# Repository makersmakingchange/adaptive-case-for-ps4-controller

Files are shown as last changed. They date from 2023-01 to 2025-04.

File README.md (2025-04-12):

# Adaptive Case for PS4 Controller
The Adaptive Case for PS4 Controller is an inexpensive and non-destructive controller modification designed to make the stock PS4 controller more accessible. This device aims to assist those with limited hand dexterity by enlarging and spreading out the buttons on the PS4 controller. This device can be mounted to a surface so that both hands can freely operate the controls.   

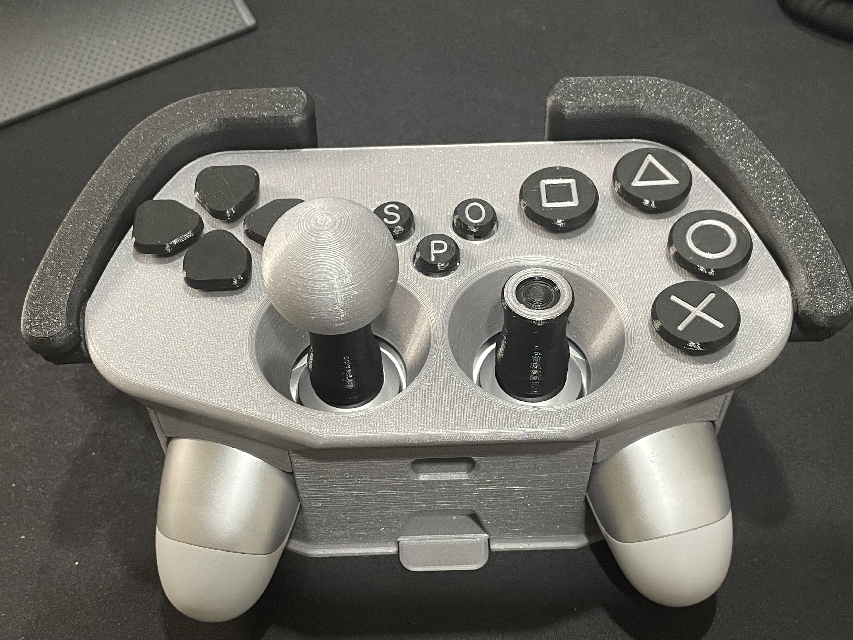
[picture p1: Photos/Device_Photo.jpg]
Picture of a black and gray Adaptive Case for PS4 Controller


## More info at
- [Makers Making Change Project Page](https://makersmakingchange.com/project/adaptive-case-for-ps4-controller)

## How to Obtain an Adaptive Case for PS4 Controller
### 1. Do it Yourself (DIY) or Do it Together (DIT)

This is an open-source assistive technology, so anyone is free to build it. All of the files and instructions required to build the Adaptive Case for PS4 Controller are contained within this repository. Refer to the Maker Checklist below.

### 2. Request a build of this device

If you would like to obtain an Adaptive Case for PS4 Controller , you may submit a build request through the [MMC Library Page](https://makersmakingchange.com/project/adaptive-case-for-ps4-controller/). The requestor is responsible for the cost of materials and any shipping.

### 3. How to build this device for someone else

If you have the skills and equipment to build this device, and would like to donate your time to create the switch for someone who needs it, visit the [MMC Maker Wanted](https://makersmakingchange.com/maker-wanted/) section.

## Getting Started

### 1. Read the Makers Checklist

The Makers Checklist contains a list of tasks to complete to build the device.

### 2. Print the 3D Printable components

All of the files and individual print files can be in the [/Build_Files/3D_Printing_Files](/Build_Files/3D_Printing_Files/) folder.

### 3. Assemble the Adaptive Case for PS4 Controller

Reference the [Assembly Guide](/Documentation/Adaptive_Case_for_Ps4_Controller_Assembly_Guide.pdf) for the tools and steps required to build each portion.

## Files
### Documentation
| Document             | Version | Link |
|----------------------|---------|------|
| Design Rationale     | 1.0     | [Adaptive_Case_for_Ps4_Controller_Design_Rationale](/Documentation/Adaptive_Case_for_Ps4_Controller_Design_Rationale.pdf)     |
| Maker Checklist      | 1.0     | [Adaptive_Case_for_Ps4_Controller_Maker_Checklist](/Documentation/Adaptive_Case_for_Ps4_Controller_Maker_Checklist.pdf)     |
| Bill of Materials    | 1.0     | [Adaptive_Case_for_Ps4_Controller_Bill_of_Materials](/Documentation/Adaptive_Case_for_Ps4_Controller_BOM.xlsx)     |
| 3D Printing Guide    | 1.0     | [Adaptive_Case_for_Ps4_Controller_3D_Printing_Guide](/Documentation/Adaptive_Case_for_Ps4_Controller_3D_Printing_Guide.pdf)   |
| Assembly Guide       | 1.0     | [Adaptive_Case_for_Ps4_Controller_Assembly_Guide](/Documentation/Adaptive_Case_for_Ps4_Controller_Assembly_Guide.pdf)     |
| User Guide           | 1.0     | [Adaptive_Case_for_Ps4_Controller_User_Guide](/Documentation/Adaptive_Case_for_Ps4_Controller_User_Guide.pdf)    |
| Changelog            | 1.0     | [Adaptive_Case_for_Ps4_Controller_Changelog](/Documentation/Adaptive_Case_for_Ps4_Controller_Changelog.pdf)     |

### Design Files
- [CAD Files](/Design_Files)

### Build Files
 - [3D Printing Files](/Build_Files/3D_Printing_Files)

## Attribution

Design: [Cisco](https://www.printables.com/social/28161-cisco/models) posted on [Printables](https://www.printables.com/model/91884-ps4-case-adapter)

Documentation by Neil Squire / Makers Making Change.

## License
Everything needed or used to design, make, test, or prepare theAdaptive_Case_for_Ps4_Controller is licensed under the CERN 2.0 Permissive license <https://ohwr.org/project/cernohl/wikis/Documents/CERN-OHL-version-2> (CERN-OHL-P) . 

Accompanying material such as instruction manuals, videos, and other copyrightable works that are useful but not necessary to design, make, test, or prepare the Adaptive_Case_for_Ps4_Controller are published under a Creative Commons Attribution-ShareAlike 4.0 license https://creativecommons.org/licenses/by-sa/4.0/ (CC BY-SA 4.0).

---

<!-- ABOUT MMC START -->
## About Makers Making Change
[Makers Making Change Logo](https://www.makersmakingchange.com/)

Makers Making Change is a program of [Neil Squire](https://www.neilsquire.ca/), a Canadian non-profit that uses technology, knowledge, and passion to empower people with disabilities.

Makers Making Change leverages the capacity of community based Makers, Disability Professionals and Volunteers to develop and deliver affordable Open Source Assistive Technologies.

 - Website: [www.MakersMakingChange.com](https://www.makersmakingchange.com/)
 - GitHub: [makersmakingchange](https://github.com/makersmakingchange)
 - Bluesky: [@makersmakingchange.bsky.social](https://bsky.app/profile/makersmakingchange.bsky.social)
 - Instagram: [@makersmakingchange](https://www.instagram.com/makersmakingchange)
 - Facebook: [makersmakechange](https://www.facebook.com/makersmakechange)
 - LinkedIn: [Neil Squire Society](https://www.linkedin.com/company/neil-squire-society/)
 - Thingiverse: [makersmakingchange](https://www.thingiverse.com/makersmakingchange/about)
 - Printables: [MakersMakingChange](https://www.printables.com/@MakersMakingChange)

### Contact Us
For technical questions, to get involved, or to share your experience we encourage you to [visit our website](https://www.makersmakingchange.com/) or [contact us](https://www.makersmakingchange.com/s/contact).
<!-- ABOUT MMC END -->

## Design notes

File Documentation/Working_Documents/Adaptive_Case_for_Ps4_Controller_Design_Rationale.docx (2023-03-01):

# Introduction

The Adaptive Case for PS4 Controller is an inexpensive and non-destructive controller modification designed to make the stock PS4 controller more accessible. This device aims to assist those with limited hand dexterity by enlarging and spreading out the buttons on the PS4 controller. This device can be mounted to a surface so that both hands can freely operate the controls.

# Research

Device | Price | Notes | Link

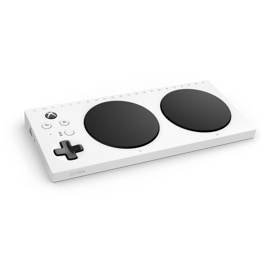
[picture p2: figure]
Angled view of Xbox Adaptive Controller

XAC – Commercial | ~$130 CA | The Xbox adaptive controller allows users with limited dexterity fully customize their gaming set up with different assistive switches and joysticks. This device costs around $130 plus the additional cost of external devices. | Xbox Adaptive Controller | Xbox (https://www.xbox.com/en-CA/accessories/controllers/xbox-adaptive-controller)

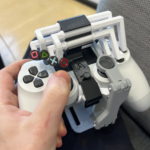
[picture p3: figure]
A hand holding a white PS4 controller with 3D printed one handed controls

One Handed Ps4 Controller | DIY | This DIY device is inexpensive and fully 3D printed. It targets users with one hand or users with more dexterity in one hand. | One-handed DualShock 4 by Akaki | Download free STL model | Printables.com (https://www.printables.com/model/126646-one-handed-dualshock-4) One-handed PS4 Controller Modification - Makers Making Change (https://makersmakingchange.com/project/one-handed-ps4-controller-modification/)

# Requirements

## Goals

G01 | Allow users with limited hand dexterity operate the PS4 controller
G02 | Nondestructively modify the PS4 controller to make it more accessible
G03 | Assist users who find it challenging to hold a controller

## Functional Requirements

F01 | Must fit the standard PS4 controller (DualShock 4)
F02 | Must allow users to operate the PS4 controller with limited dexterity and force

## Non-functional Requirement

NF01 | Must be easy to clean

## Constraints

C01 | Must be printable on standard Maker 3D printers

# Version 1.0

The Adaptive Case for PS4 Controller is designed by Cisco (https://www.printables.com/social/28161-cisco/models) on Printables (https://www.printables.com/model/91884-ps4-case-adapter) under the GNU GENERAL PUBLIC LICENSE (https://www.gnu.org/licenses/old-licenses/gpl-2.0.html).

This device encapsulates the controller in an adaptive case that can be mounted to a surface, so users do not need to hold the controller. It has multiple joystick options to help tailor the device to the user.

## Device Testing

### Assembling

- Little difficult to feed in Button Tails
  - Broke R1 tail while feeding into its slot.
  - Using sandpaper to smooth rough parts on these tails helps.
  - Using a zip tie to clear the tunnels also helps.
  - May take a few extra tails to install properly.
  - Once installed, they work great.
- Joysticks
  - Very secure when properly attached.
  - Very difficult to thread screws into joystick toppers.
  - Broke two different mounting screw while attaching the joysticks to the controller.
  - Threads broke off inside the joystick toppers. All had to be reprinted.

Notes: The designer has been contacted and is willing to modify the print files so threads can be printed sideways to increase strength. The designer will also increase the thread tolerances to make the joysticks easier to attach.

Update: Fusion360 files have been updated to add 0.15mm clearance to the joystick threads. This has been tested on multiple printers and is working well.

### Operating

- All buttons worked as intended.

# Opportunities for Improvement

- Allow Touch Pad to be pressed.
- As only L2 and R2 bumpers can be triggered, it would be nice to allow access to the L1 and R1 bumpers.

© 2023 by Neil Squire / Makers Making Change This work is licensed under the CC BY SA 4.0 License: http://creativecommons.org/licenses/by-sa/4.0 Files available at https://makersmakingchange.com/project/adaptive-case-for-ps4-controller Page 1 of 1

V1.0 | February 2023 Adaptive Case for PS4 Controller Design Rationale

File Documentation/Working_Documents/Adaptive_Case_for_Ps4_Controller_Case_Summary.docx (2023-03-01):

# Title

Adaptive Case for PS4 Controller

## Subtitle

An inexpensive and non-destructive controller modification designed to make the stock PS4 controller more accessible.

Device Specifications

Build Time:

< 1hr

1-4 hr

5-10hr

>10hr

Cost:

$0 - $10

$11 - $25

$26 - $50

$51 - $100

$101 - $250

$250+

Stage: Recently Added

Skills: 3D Printing

Need:

Disability: Mobility / Physical

Difficulty: Intermediate

License: GNU GENERAL PUBLIC LICENSE (https://www.gnu.org/licenses/old-licenses/gpl-2.0.html)

Usages: ADL, Recreation and Leisure, Computer Access

Type:

Designer:

## Device Details

### Overview

The Adaptive Case for PS4 Controller is an inexpensive and non-destructive controller modification designed to make the stock PS4 controller more accessible. This device aims to assist those with limited hand dexterity by enlarging and spreading out the buttons on the PS4 controller. This device can be mounted to a surface so that both hands can freely operate the controls.

### Compatibility

Note that the PS4 controller can be used for PC based gaming.

Platforms: PlayStation 4, PC

Controllers: DualShock 4 Controller

### Usage

The case can be opened to insert the PS4 controller and snapped shut to secure it. 3D printed mounting screws are placed around the joysticks on the controller before screwing on various attachments. The device also comes with a low-profile dock that can be used to secure the adaptive case to a surface.

### Cost

Approximately $8 for filament

### Build Instructions

The build involves assembling 3D printed components. No commercial hardware is needed.

#### Skills Required

- 3D Printing

#### Time Required

- Total 3D Printing Time: 38h 20min
- Assembly Time: 10m

#### Tools

- Eye Protection
- Hobby Knife
- Sandpaper
- Superglue
- Tape
- Zip Ties

#### 3D Printing

- 1X All_Button_Faces.stl
- 1X Button_Tails.stl
- 1X Case.stl
- 1X Dock.stl
- 1X Face.stl
- 1X Joystick.stl
- 1X Trigger.stl

### Attribution

Design by Cisco (https://www.printables.com/social/28161-cisco/models) posted on Printables (https://www.printables.com/model/91884-ps4-case-adapter) under the GNU GENERAL PUBLIC LICENSE (https://www.gnu.org/licenses/old-licenses/gpl-2.0.html)

Documentation: Neil Squire / Makers Making Change

© 2023 by Neil Squire / Makers Making Change This work is licensed under the CC BY SA 4.0 License: http://creativecommons.org/licenses/by-sa/4.0 Files available at https://makersmakingchange.com/project/adaptive-case-for-ps4-controller Page 1 of 4

V1.0 | February 2023 Adaptive Case for PS4 Controller Summary

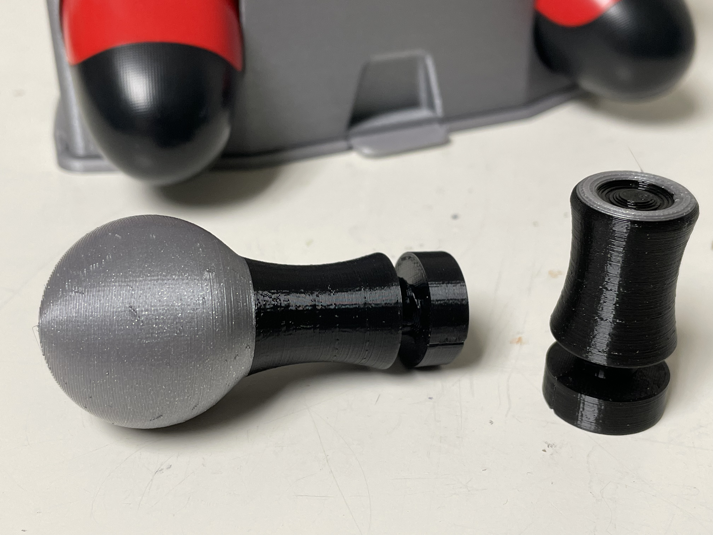
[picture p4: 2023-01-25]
Photos/Joysticks.jpeg

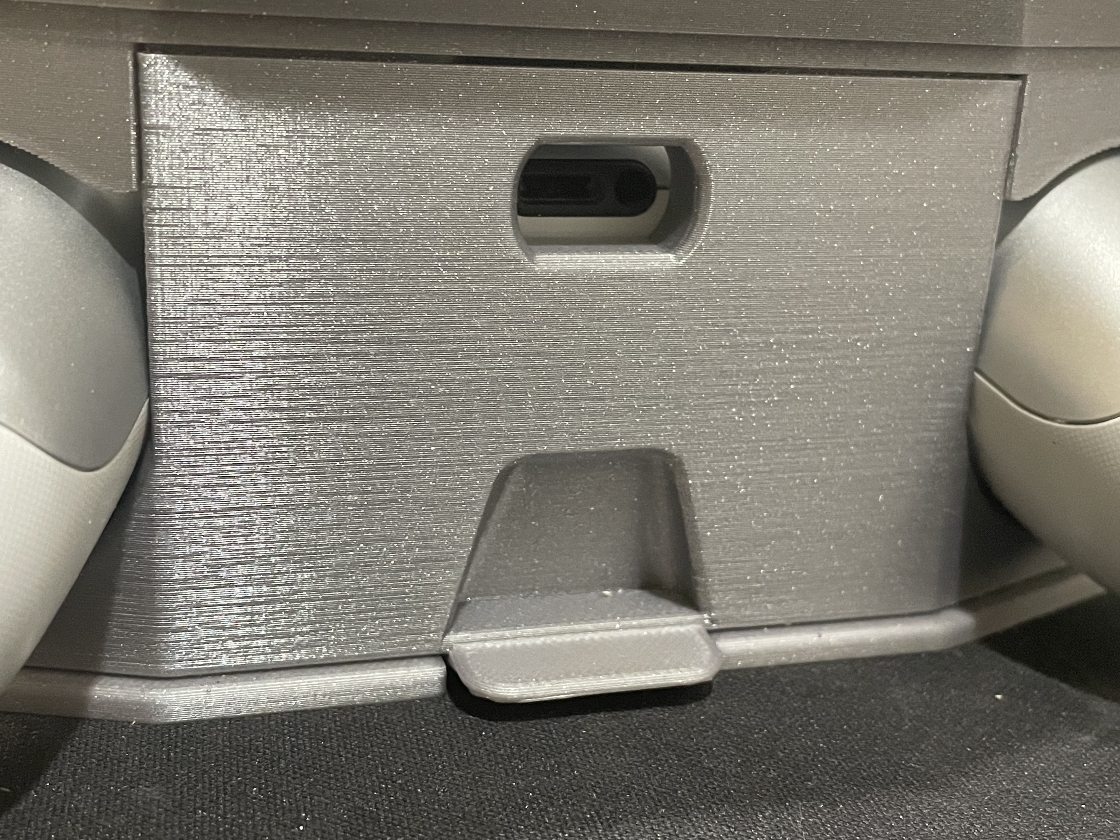
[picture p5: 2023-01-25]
Photos/Unlocking Dock.jpeg

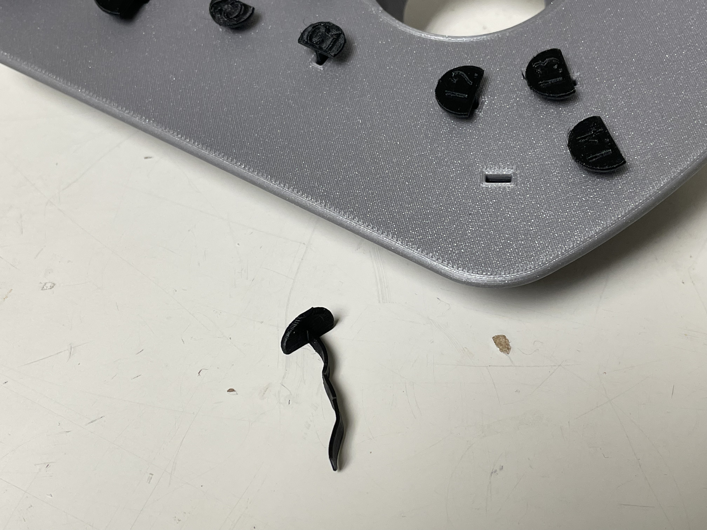
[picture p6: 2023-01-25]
Photos/Broken Tail.jpg

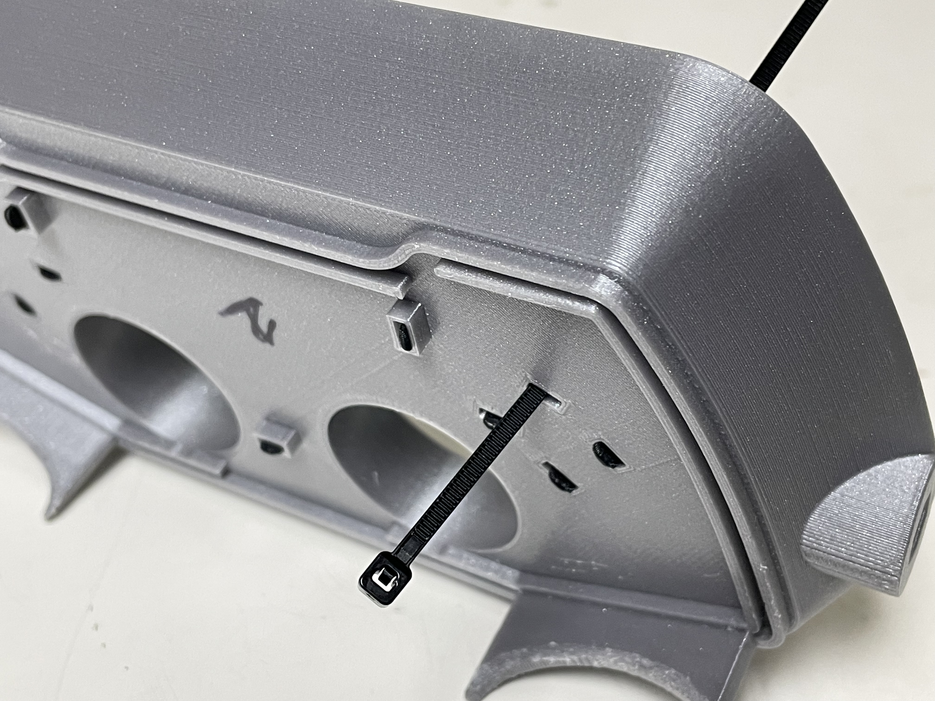
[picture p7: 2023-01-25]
Photos/Plugged Tunnel.jpg

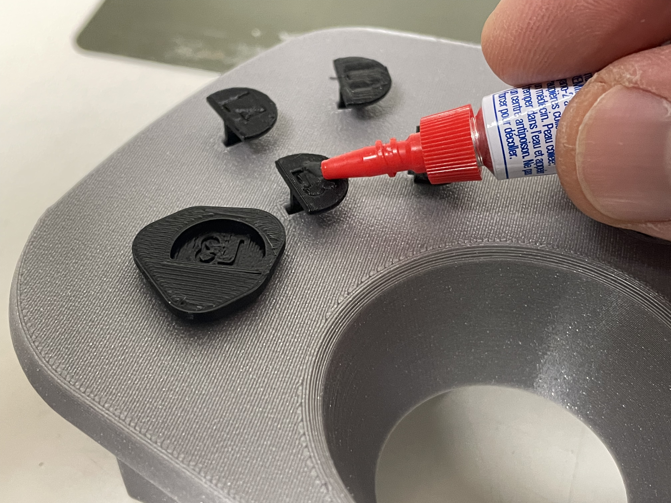
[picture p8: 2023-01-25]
Photos/Gluing Button Faces.jpg

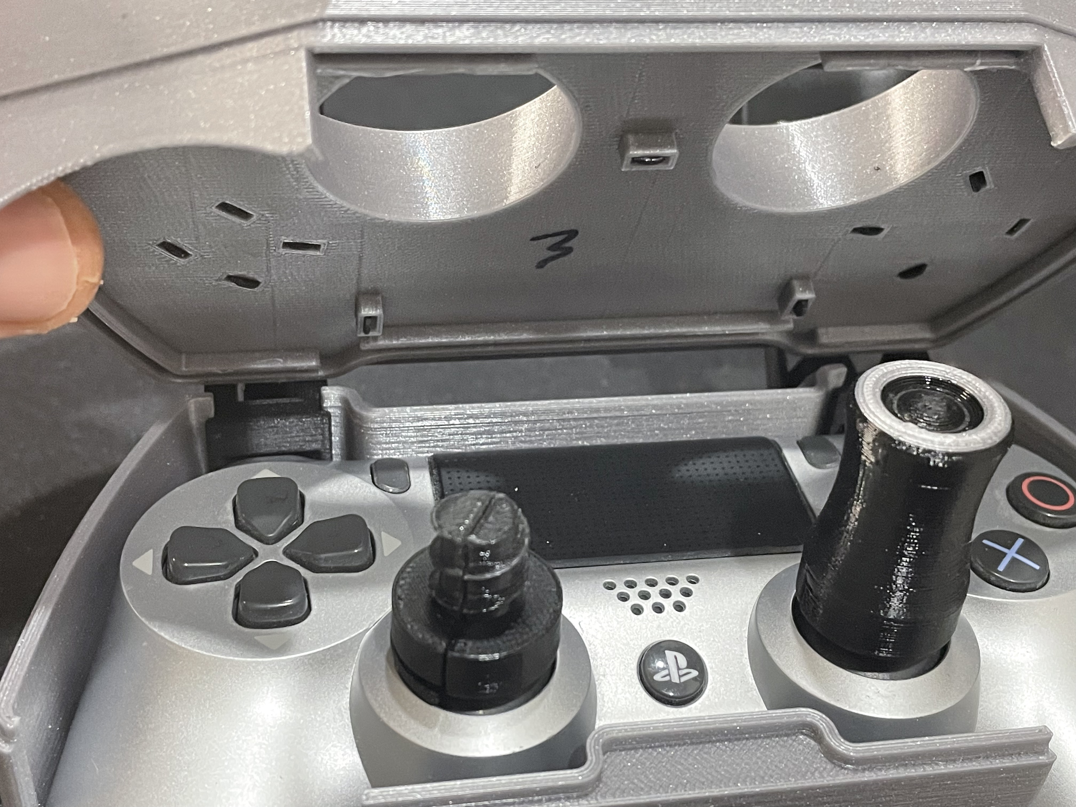
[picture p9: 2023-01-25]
Photos/Opening Face.jpeg

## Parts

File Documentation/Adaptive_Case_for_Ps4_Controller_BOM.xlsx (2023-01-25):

Adaptive Case for PS4 Controller |  |  |  |  |  |  |  | Unit Cost | Total Cost | Total Print time (hr) | Total filament (g)
Version: V1.0 |  | Last Updated: 2023-Jan-27 |  |  |  |  |  | $7.50 | $0.00 | 38.33 | 208
Commercial Parts
ID | Part Name | Part Type | QTY | QTY/PKG | $/PKG | PKG QTY | $/Unit | Extended | Total | Link
 | Not Required
3D Printed Parts ESTIMATED PRICING USING 1KG ROLL COST: |  | $25.00
ID | Part | Material | QTY | Mass (g) / Unit | Time / Unit |  | Print Time (Min) | Estimated Price |  | Link
 | All_Button_Faces.stl | PLA | 1 | 7 | 65 |  | 65 | $0.18
 | Button_Tails.stl | PETG (PLA if unavalible) | 1 | 3 | 32 |  | 32 | $0.07
 | Case.stl | PLA | 1 | 71 | 596 |  | 596 | $1.77
 | Dock.stl | PLA | 1 | 31 | 224 |  | 224 | $0.78
 | Face.stl | PLA | 1 | 96 | 610 |  | 610 | $2.40
 | Joystick.stl | PLA | 1 | 47 | 389 |  | 389 | $1.18
 | Trigger.stl | PLA | 1 | 45 | 384 |  | 384 | $1.12
Custom Printed Circuit Board (PCB)
ID | Part |  | QTY
 | Not Required
Tools for Assembly
 | Super Glue
 | Tape
 | Zip Tie
 | Safety Knife
Alternatives (if there are other sources for some parts link them below)
ID | Part and description |  |  |  |  |  |  |  |  | Link

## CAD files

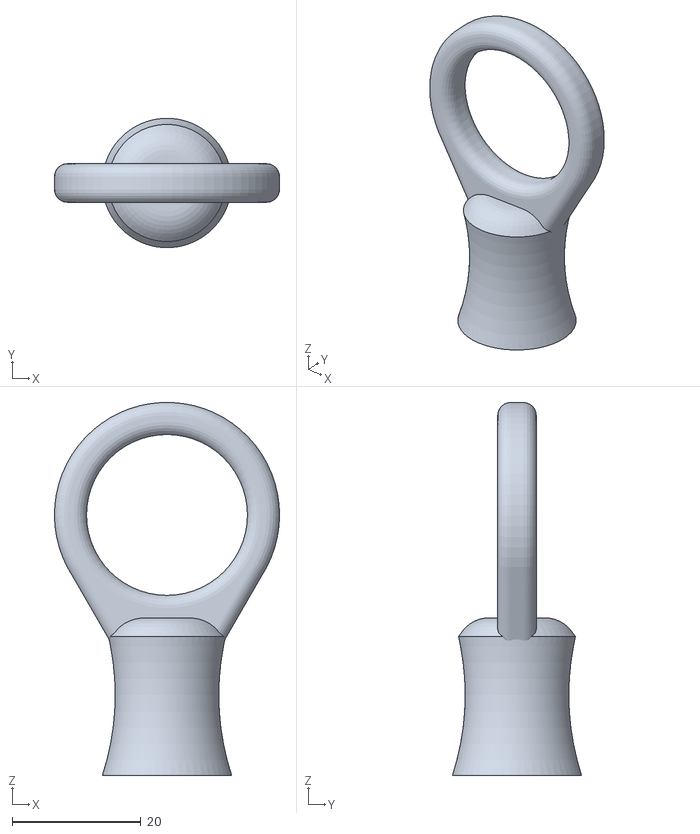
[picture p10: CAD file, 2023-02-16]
Build_Files/3D_Printing_Files/Individual_Joystick_Print_Files/Ring_Joystick.stl
35.0 x 20.1 x 58.0

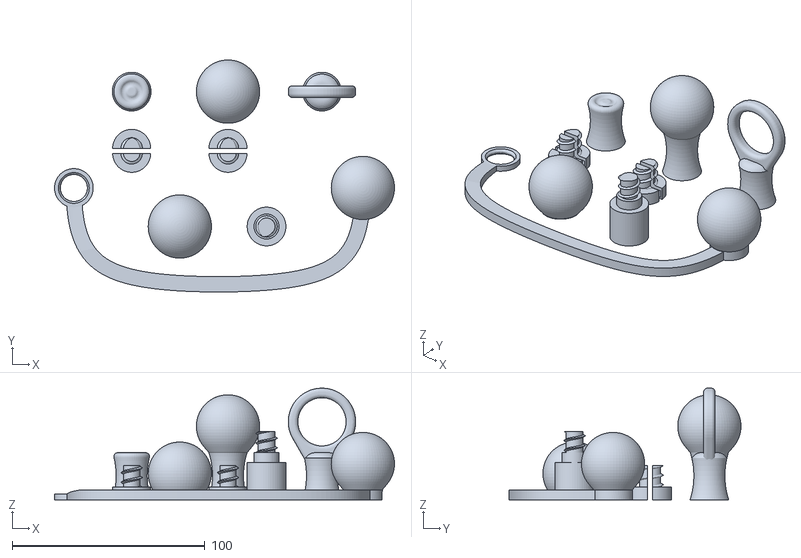
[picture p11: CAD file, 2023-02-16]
Build_Files/3D_Printing_Files/Joysticks.stl
176.5 x 120.4 x 58.0

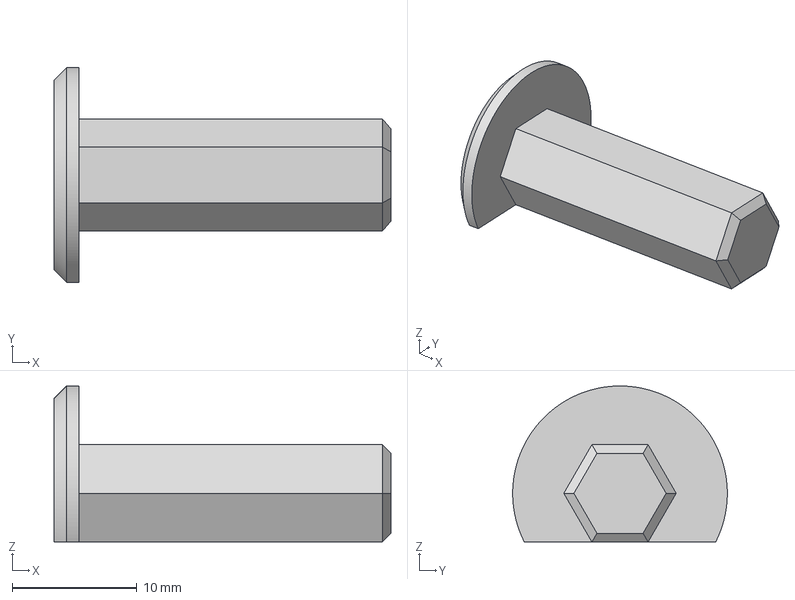
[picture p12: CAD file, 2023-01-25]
Design_Files/3mf Raw Files/trigershaftl.3mf
27.0 x 17.2 x 12.5 mm

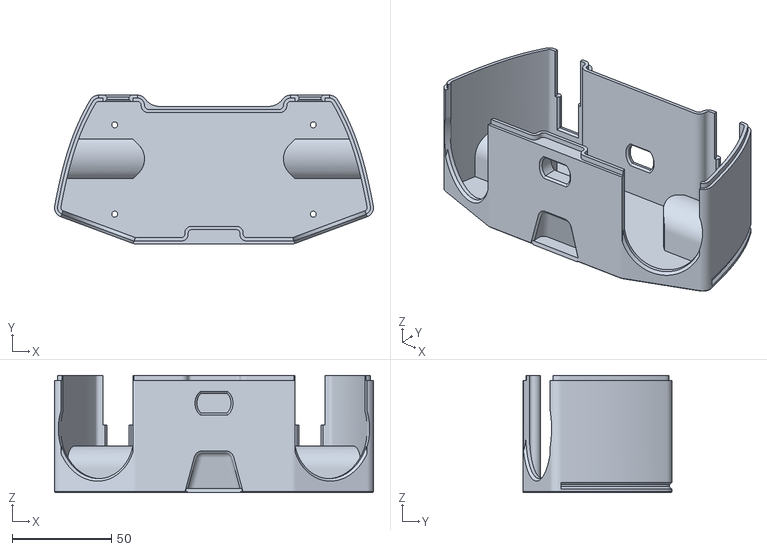
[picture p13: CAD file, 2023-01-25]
Build_Files/3D_Printing_Files/Case.stl
160.7 x 75.0 x 59.0

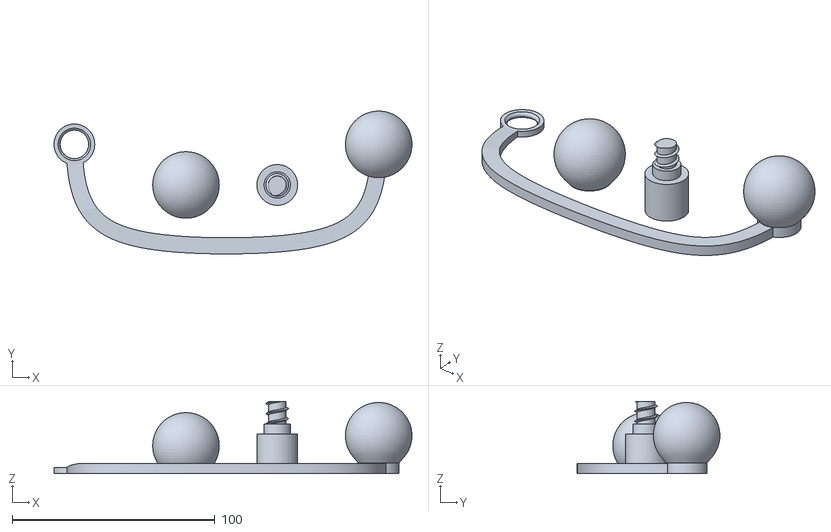
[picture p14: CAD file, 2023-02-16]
Build_Files/3D_Printing_Files/Individual_Joystick_Print_Files/Double_Joystick.stl
176.5 x 70.4 x 35.5

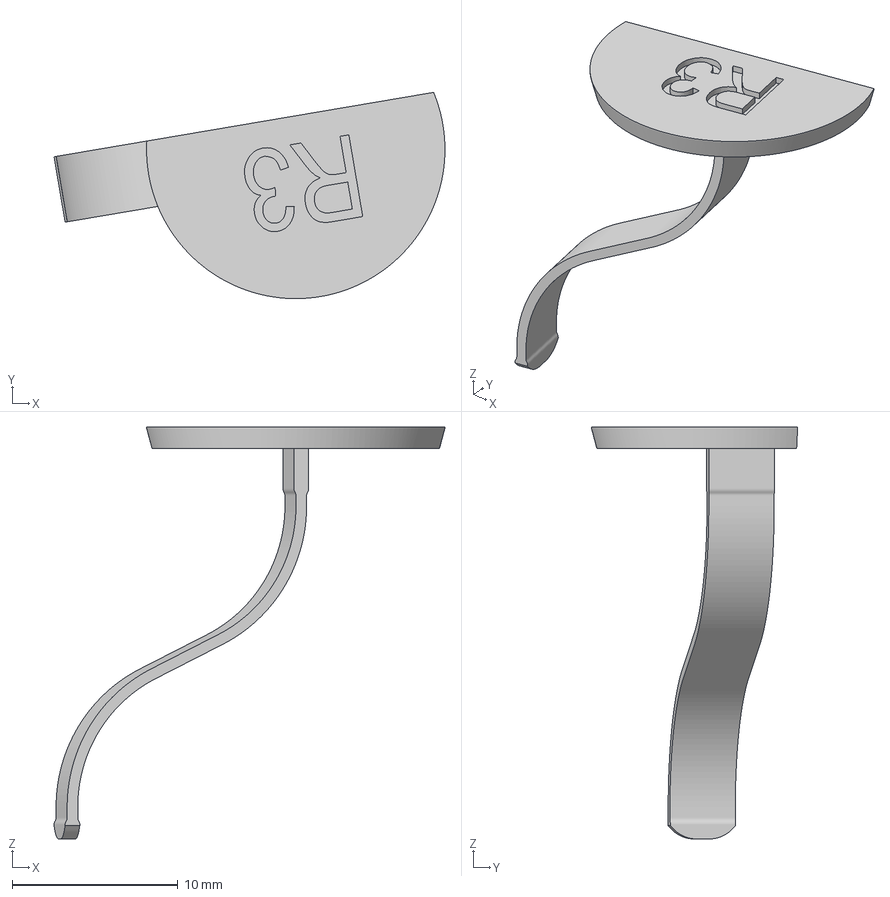
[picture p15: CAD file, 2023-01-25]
Design_Files/3mf Raw Files/buttontailr3.3mf
23.6 x 12.4 x 24.8 mm

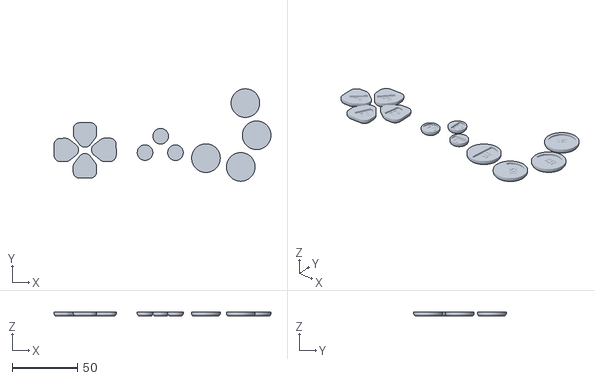
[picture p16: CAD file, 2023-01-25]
Build_Files/3D_Printing_Files/All_Button_Faces .stl
166.4 x 71.0 x 3.00

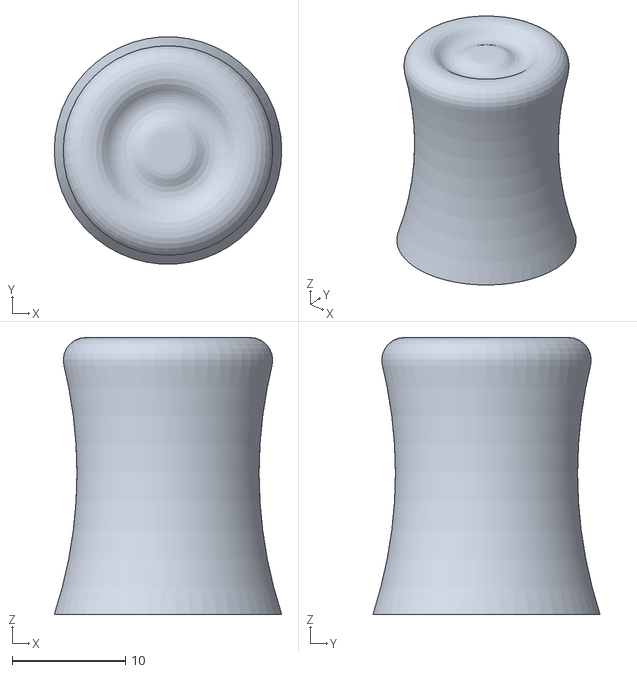
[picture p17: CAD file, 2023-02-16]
Build_Files/3D_Printing_Files/Individual_Joystick_Print_Files/Extended_Joystick.stl
20.1 x 20.1 x 24.5

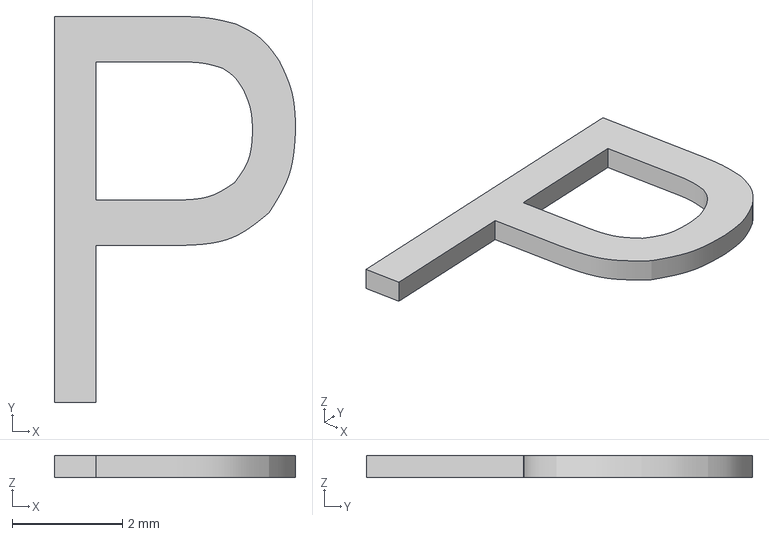
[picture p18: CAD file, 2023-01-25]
Design_Files/3mf Raw Files/buttonletterc3.3mf
4.38 x 7.00 x 0.4 mm

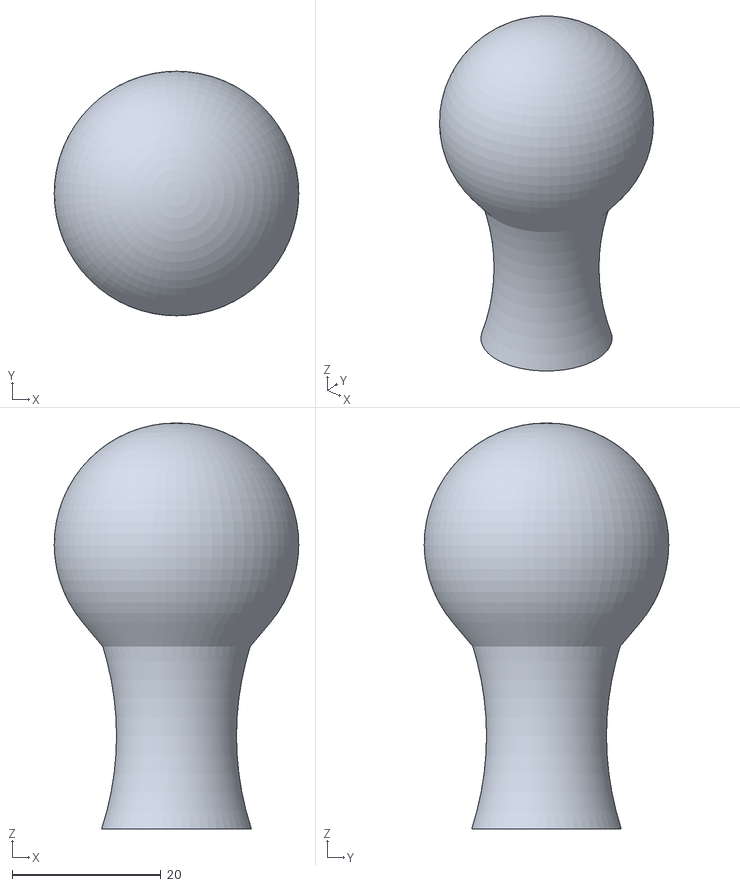
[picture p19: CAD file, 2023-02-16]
Build_Files/3D_Printing_Files/Individual_Joystick_Print_Files/Ball Joystick.stl
32.8 x 32.8 x 54.5

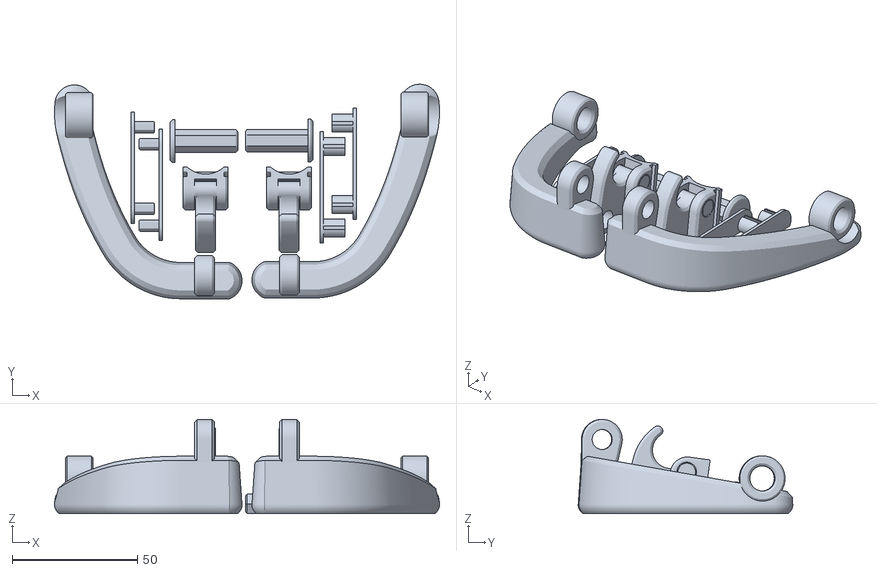
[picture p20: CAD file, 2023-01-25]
Build_Files/3D_Printing_Files/Trigger.stl
153.5 x 85.6 x 37.5

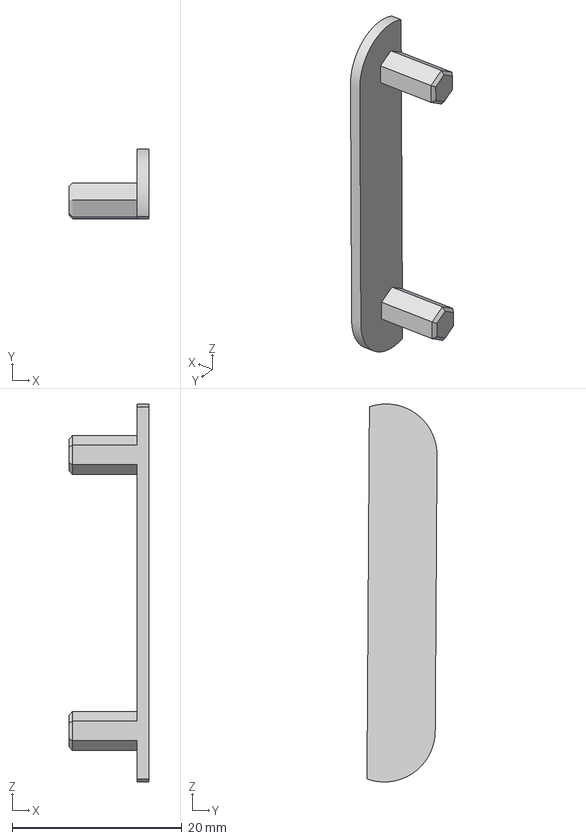
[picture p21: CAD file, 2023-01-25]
Design_Files/3mf Raw Files/trigerlink2r.3mf
9.40 x 8.25 x 44.5 mm

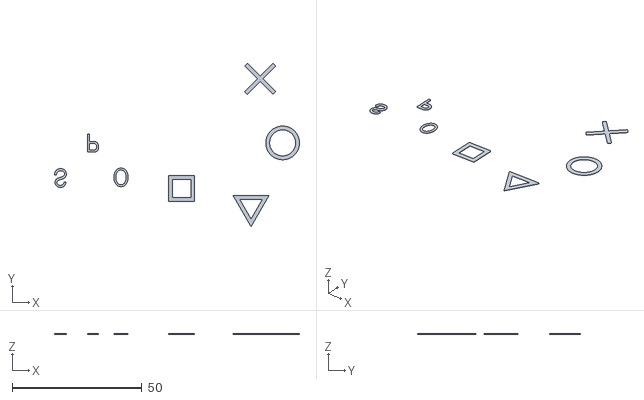
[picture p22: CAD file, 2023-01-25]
Build_Files/3D_Printing_Files/All_Button_Faces_Lettering_(optional).stl
94.4 x 63.0 x 0.4

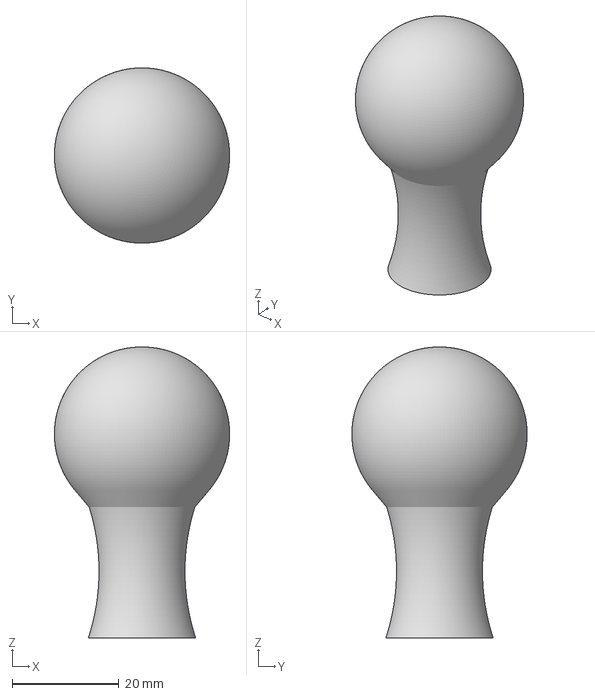
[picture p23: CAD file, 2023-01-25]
Design_Files/3mf Raw Files/joystickboll.3mf
32.8 x 32.8 x 54.5 mm

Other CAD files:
Build_Files/3D_Printing_Files/Button_Tails.stl
Design_Files/3mf Raw Files/case.3mf
Build_Files/3D_Printing_Files/Face.stl
Design_Files/3mf Raw Files/buttonletterr2.3mf
Build_Files/3D_Printing_Files/Dock.stl
Build_Files/3D_Printing_Files/Individual_Joystick_Print_Files/Joystick_Screws.stl
Design_Files/3mf Raw Files/buttonfacec1.3mf
Design_Files/3mf Raw Files/buttonfacec2.3mf
Design_Files/3mf Raw Files/buttonfacec3.3mf
Design_Files/3mf Raw Files/buttonfacel1.3mf
Design_Files/3mf Raw Files/buttonfacel2.3mf
Design_Files/3mf Raw Files/buttonfacel3.3mf
Design_Files/3mf Raw Files/buttonfacel4.3mf
Design_Files/3mf Raw Files/buttonfacer1.3mf
Design_Files/3mf Raw Files/buttonfacer2.3mf
Design_Files/3mf Raw Files/buttonfacer3.3mf
Design_Files/3mf Raw Files/buttonfacer4.3mf
Design_Files/3mf Raw Files/buttonletterc1.3mf
Design_Files/3mf Raw Files/buttonletterc2.3mf
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

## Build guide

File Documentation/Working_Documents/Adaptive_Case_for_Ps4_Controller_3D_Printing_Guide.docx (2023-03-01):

# 3D Printing Summary

Metrics | Adaptive Case for PS4 Controller
Total Print Time (min) | 2300 (38h 20m)
Total Number of Components | 45
Typical Total Mass (g) | 208
Typical Number of Print Setups | 7

# 3D Printing Settings

## Components to Print in PLA

Print File Name | Qty | Total Print Time (hr:min) | Mass (g) | Infill (%) | Support (Y/N) | Layer Height/ Nozzle Diameter(mm) | Notes (orientation, special settings, etc.)
All_Button_Faces.stl | 1 | 1:05 | 7 | 20 | N | 0.2/0.4 | - Print in orientation given in STL
Case.stl | 1 | 9:56 | 71 | 20 | N | 0.2/0.4 | - Print in orientation given in STL
Dock.stl | 1 | 3:44 | 31 | 20 | Y | 0.2/0.4 | - Print in orientation given in STL -Supports are required for the front tab
Face.stl | 1 | 10:10 | 96 | 20 | N | 0.2/0.4 | - Print in orientation given in STL
Joystick.stl | 1 | 6:29 | 47 | 20 | N | 0.2/0.4 | - Print in orientation given in STL
Trigger.stl | 1 | 6:24 | 45 | 20 | N | 0.2/0.4 | - Print in orientation given in STL

## Components to Print in PETG (If available)

Print File Name | Qty | Total Print Time (hr:min) | Mass (g) | Infill (%) | Support (Y/N) | Layer Height/ Nozzle Diameter(mm) | Notes (orientation, special settings, etc.)
Button_Tails.stl | 1 | 0:32 | 3 | 20 | N | 0.2/0.4 | - Print in orientation given in STL

Note: The “Button Tails” transfer the force from the buttons on the case to the buttons on the controller. Due to repeated stress, it is recommended that these components are printed in PETG to help prolong their lifespan. If unavailable, PLA can be used but the part may need to be replaced over time.

# Customization Options

Users may request their choice of print colour. It is recommended to print the “All_Button_Faces.stl” in a different colour than the “Face.stl” to help with visibility.

# Post-Processing

The “Dock” is the only component that requires support material to be removed. Inspect and ensure that all components are smooth, and holes are free of print material. Sharp edges and rough surfaces can be smoothed down with sandpaper.

# Examples of Quality Prints

## Photos of All_Button_Faces.stl

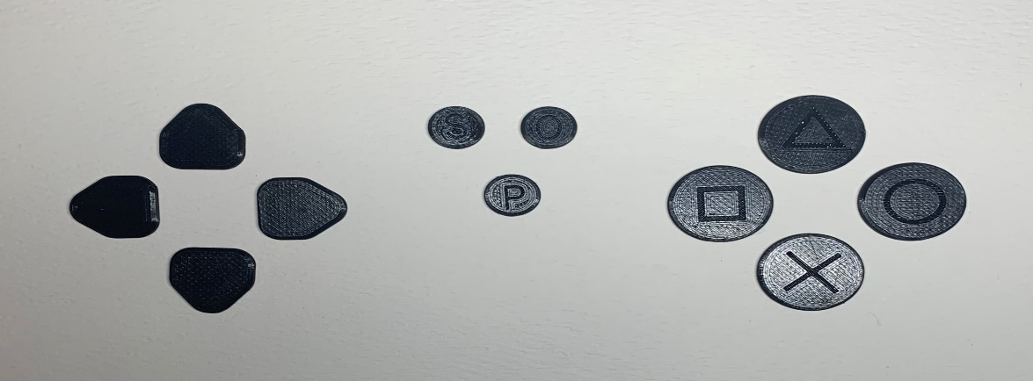
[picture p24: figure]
3D printed button faces.

## Photos of Button_Tails.stl

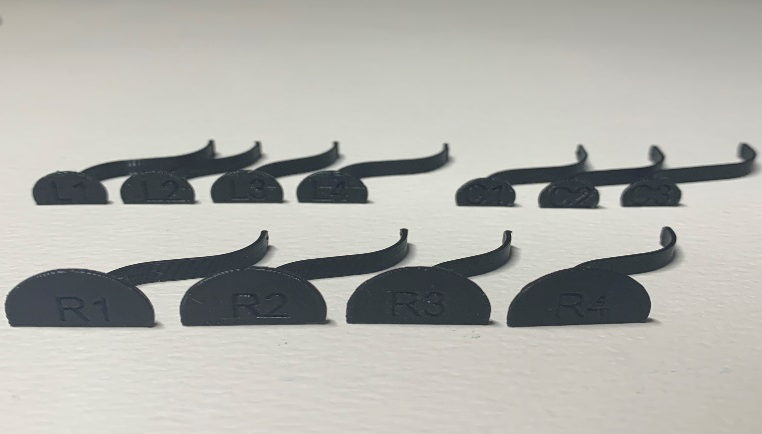
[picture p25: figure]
The front view of 3D printed button tails.
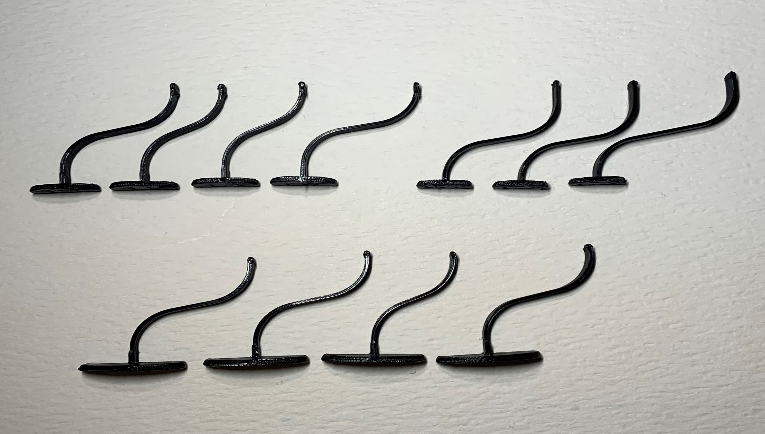
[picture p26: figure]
The top view of 3D printed button tails.

## Photos of Case.stl

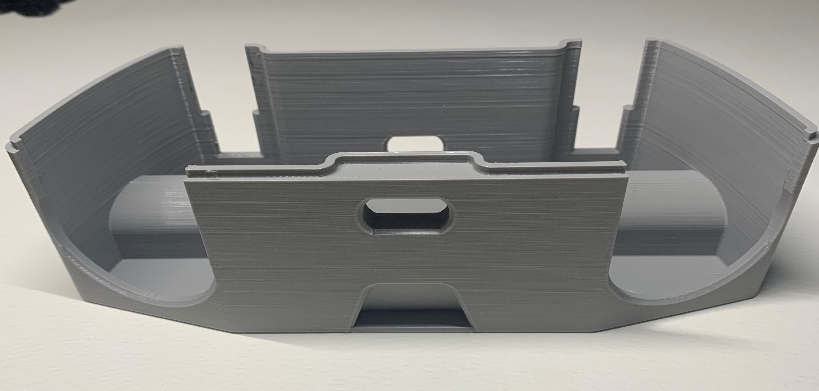
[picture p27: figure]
The front of a 3D printed Case.
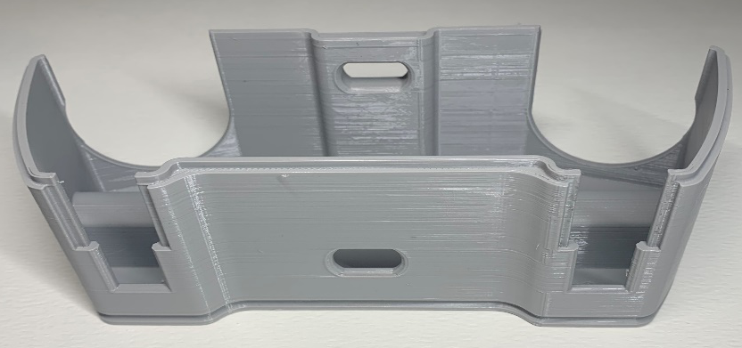
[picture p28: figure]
The back of a 3D printed case.

## Photos of Dock.stl

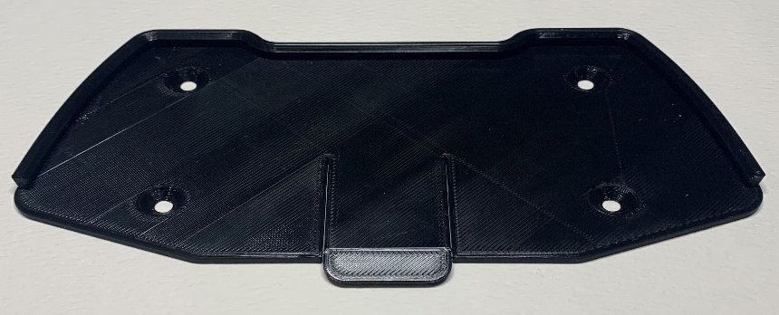
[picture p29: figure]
The top of a 3D printed dock.
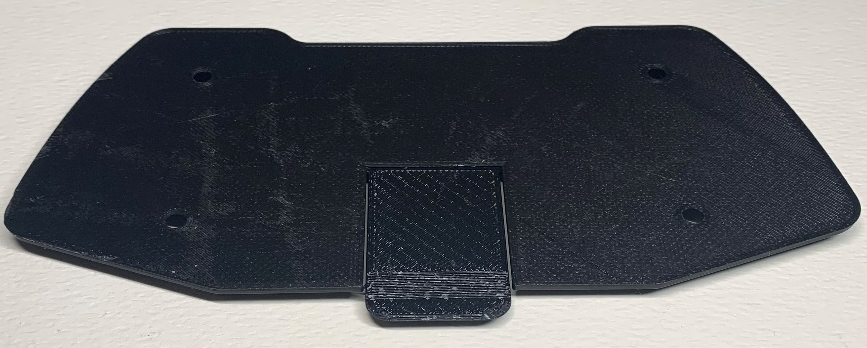
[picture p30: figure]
The bottom of a 3D printed dock.

## Photos of Face.stl

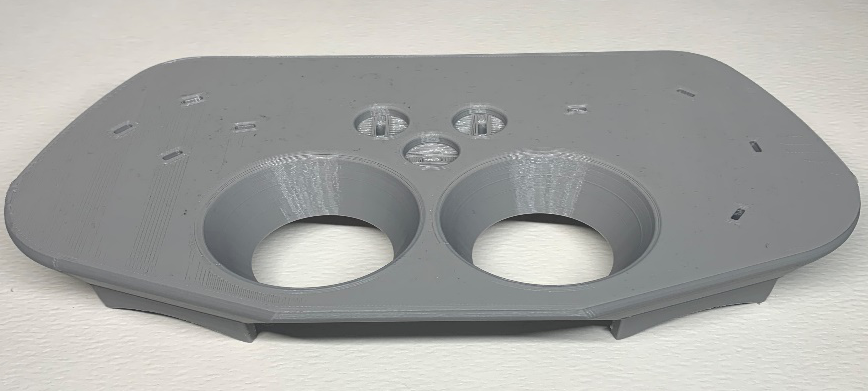
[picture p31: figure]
The top of the 3D printed face.
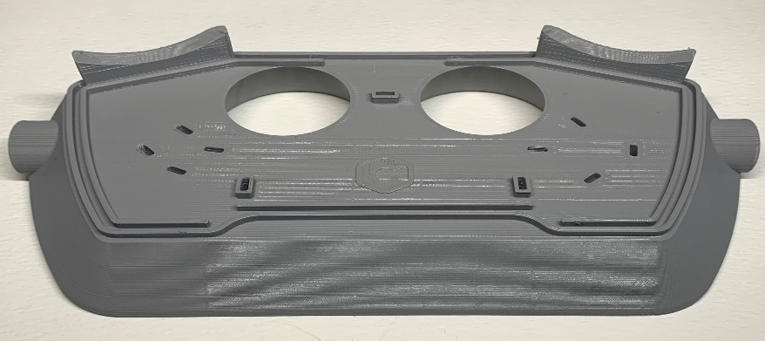
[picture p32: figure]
The bottom of a 3D printed face.

## Photos of Joystick.stl

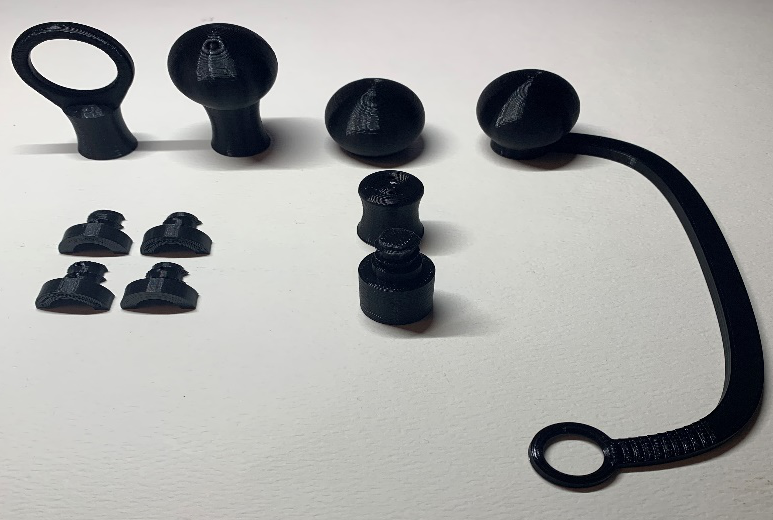
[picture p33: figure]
The front view of various joystick toppers.
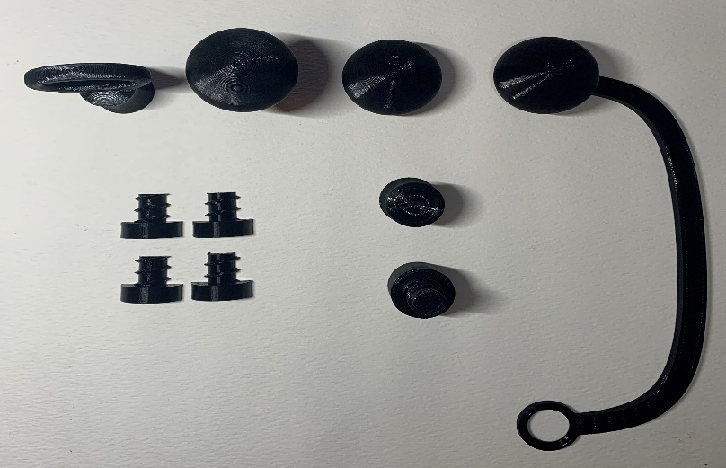
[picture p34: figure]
The top of various 3D printed joystick toppers.

## Photos of Trigger.stl

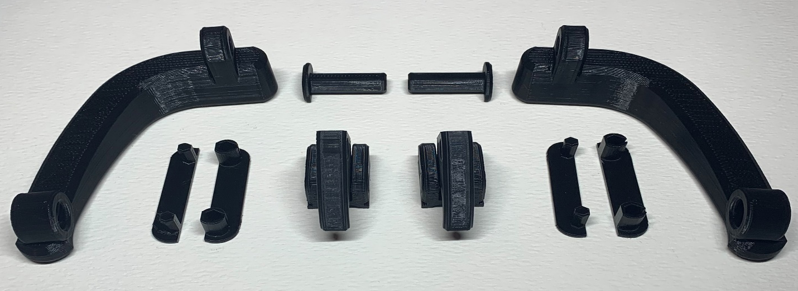
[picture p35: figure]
Various 3D printed parts to build the trigger assembly.

Note: The “Trigger Mounts” (in the centre of the photo) have print in place moving parts. Ensure that the hinge can rotate freely.

© 2023 by Neil Squire / Makers Making Change This work is licensed under the CC BY SA 4.0 License: http://creativecommons.org/licenses/by-sa/4.0 Files available at https://makersmakingchange.com/project/adaptive-case-for-ps4-controller Page 1 of 2

V1.0 | February 2023 Adaptive Case for PS4 Controller 3D Printing Guide

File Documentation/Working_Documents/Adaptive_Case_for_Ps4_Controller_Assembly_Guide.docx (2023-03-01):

# Required Components

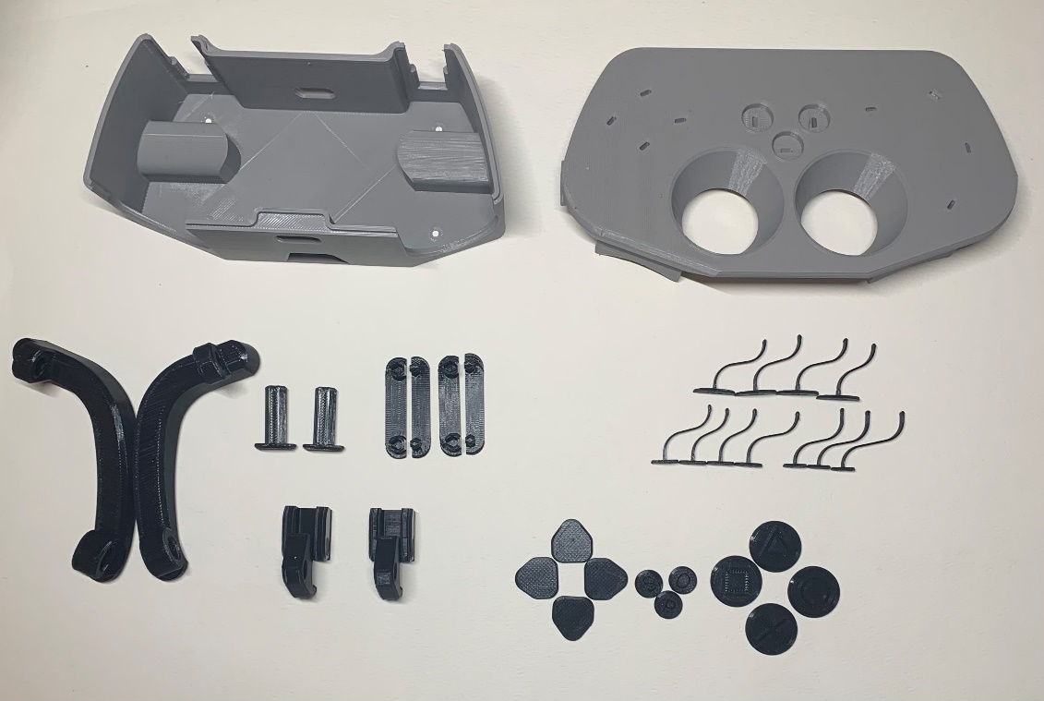
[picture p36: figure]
The 3D printed parts required to build this device.

6. 5. 2. 8. 7. 4. 3. 1. | BOM 1. Case 2. Face 3. Trigger Arm 4. Trigger Shaft 5. Trigger Link 6. Trigger Mount 7. Button Tails 8. Button Faces

# Required Tools

- Super Glue
- Tape
- Zip Tie
- Safety Knife

# Required Personal Protective Equipment (PPE)

- Safety Glasses

Note: A PS4 controller is not required for assembly but can be seen in some assembly photos.

# Assembly Instructions

## Step 1: Feeding Button Tails

Feed each “Button Tail” into its corresponding hole by matching the lettering as shown below (no swapping allowed). Hold both sides of the “Face” and feed it back and forth as needed. Progress until it shows up on the other side and sticks out about 1 mm. The tail should act as a spring when pushed. If a tunnel is too rough or a “Button Tail” breaks off inside, progress to Step 1A.

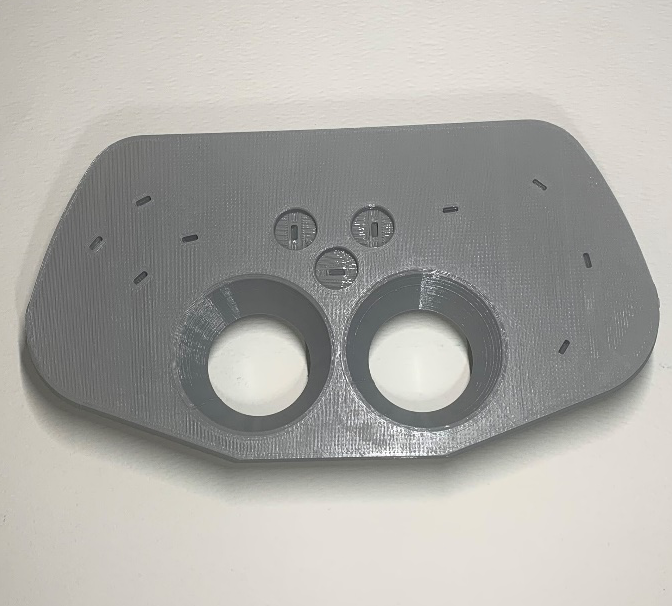
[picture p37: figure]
The face of the case with labelled inserts .
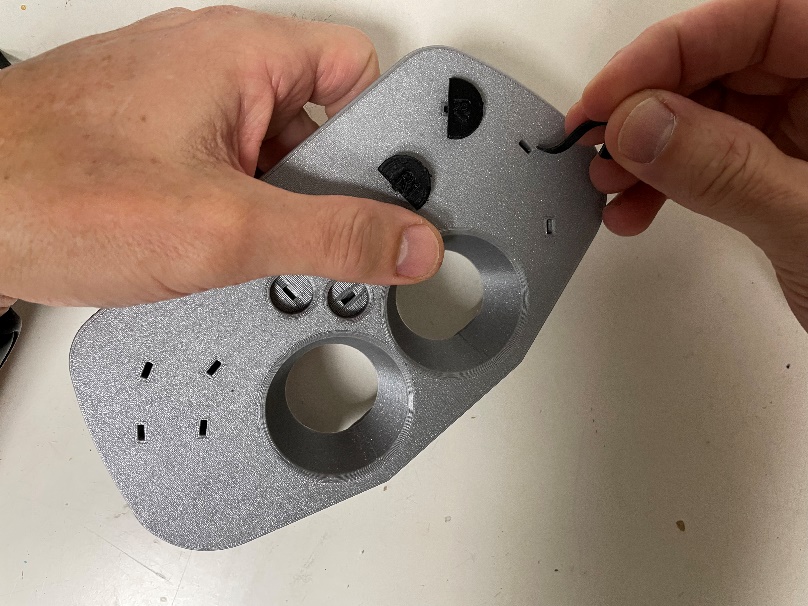
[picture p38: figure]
A hand inserting the button tales into the face.

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
## Step 1A: Fixing a Plugged Tunnel

If you get stuck on a tunnel and/or a “Button Tail” looks damaged, use a zip tie to drive through the tunnel and clear the blockage. Feed it from both sides and move it back and forth. Once resolved, proceed back to Step 1.

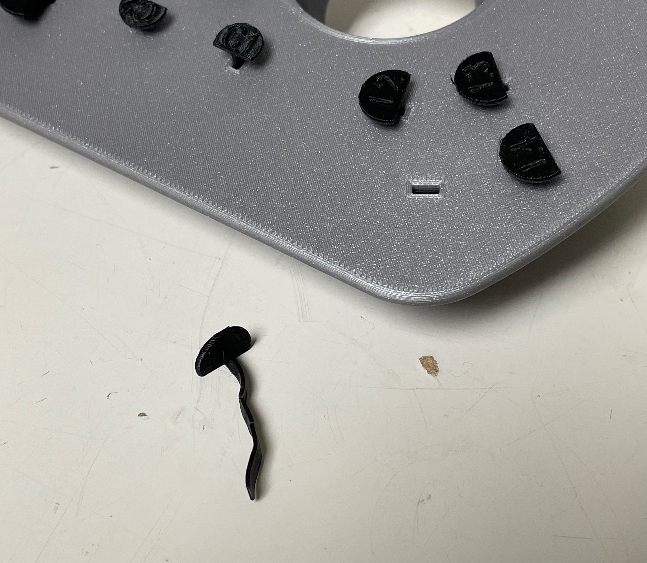
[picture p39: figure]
A broken button tail that must be replaced.
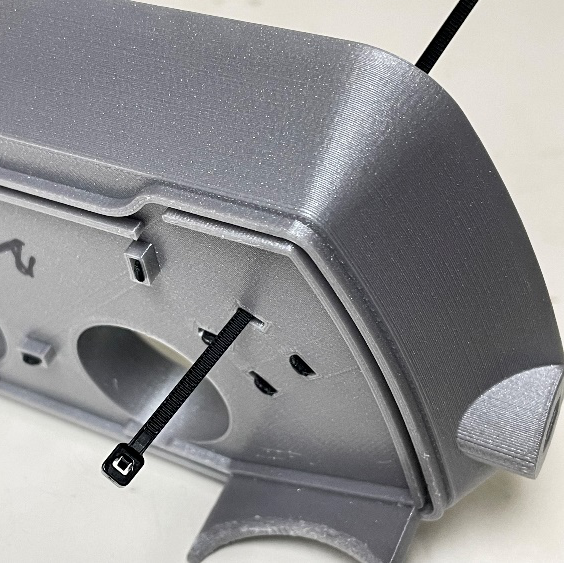
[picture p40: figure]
A zip tie being used to clear a blocked button tail tunnel.

R3

## Step 2: Installing Button Faces

Glue each “Button Face” to its corresponding “Button Tail.” The tabs on the top of the Button Tails should fit flush inside the Button Faces. Push together until the glue dries.

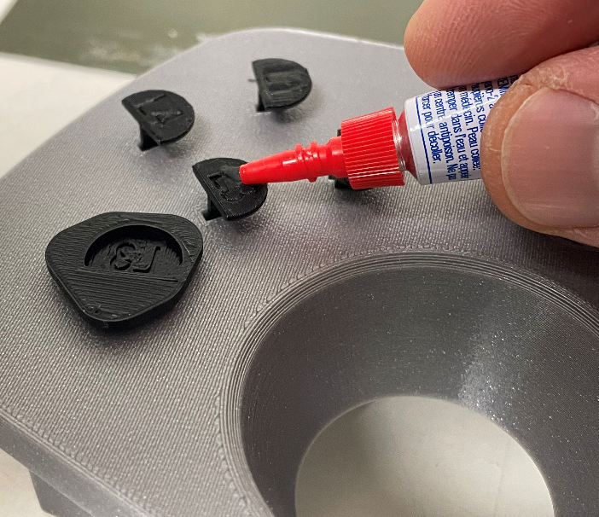
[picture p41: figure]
Super gluing the button faces onto the button tails.
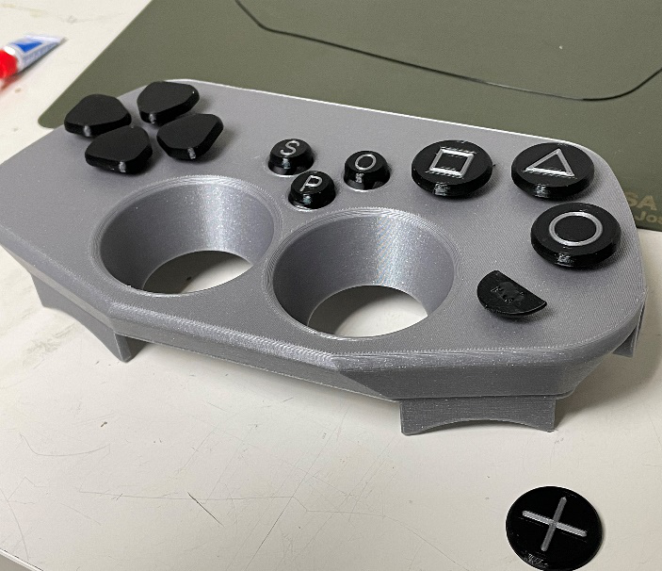
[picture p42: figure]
All the button faces installed onto their corresponding button tails resembling a completed controller layout.

## Step 3: Assembling the Triggers

Set all parts as the shown in the first picture below. Use the larger half of the “Trigger Link” to connect the “Trigger Arm” and “Trigger Mount” for each side. Insert the smaller half of the “Trigger Link” into the larger half to secure the pieces together. The two halves of the link may need to be glued together if the link wants to separate.

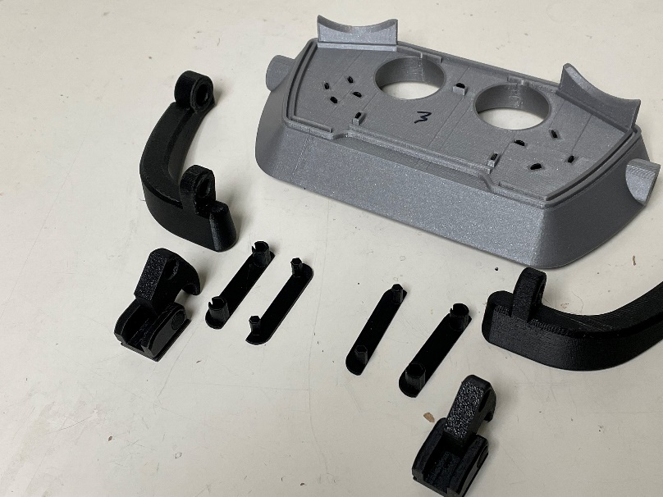
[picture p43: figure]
The parts necessary for building the trigger assembly.
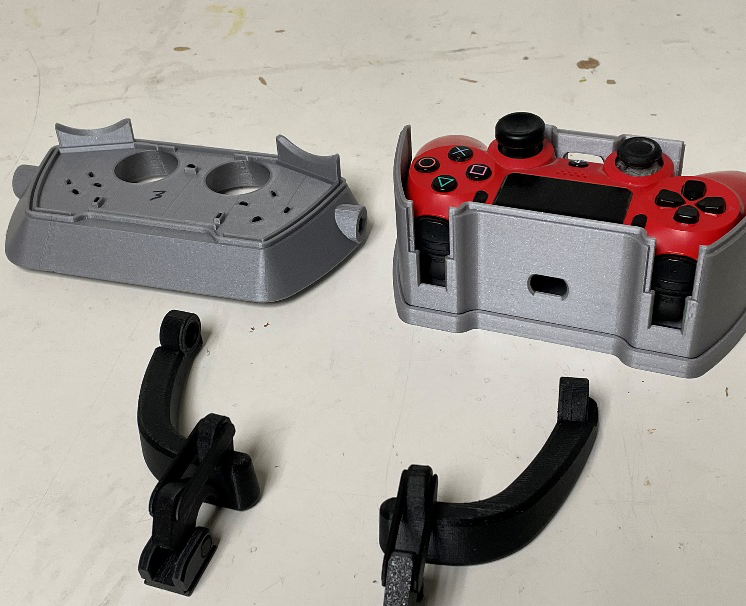
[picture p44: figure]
The triggers built and ready to be installed onto the case.

## Step 5: Mounting the Trigger to the Case

Slide the controller mounts into the slot on the back of the case as shown below. Once installed, fit the “Face” onto the top of the case.

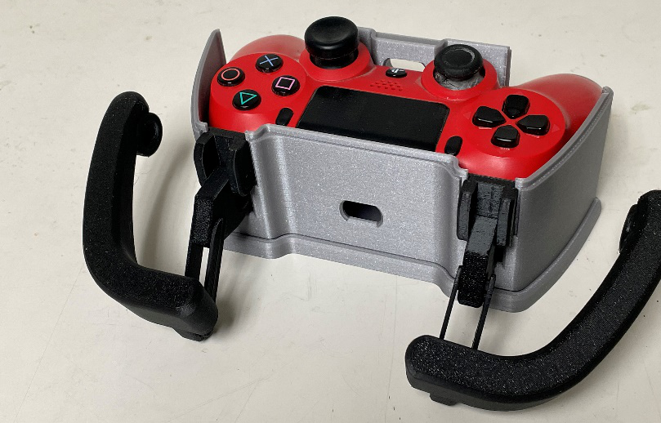
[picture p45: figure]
The first step for installed the triggers.
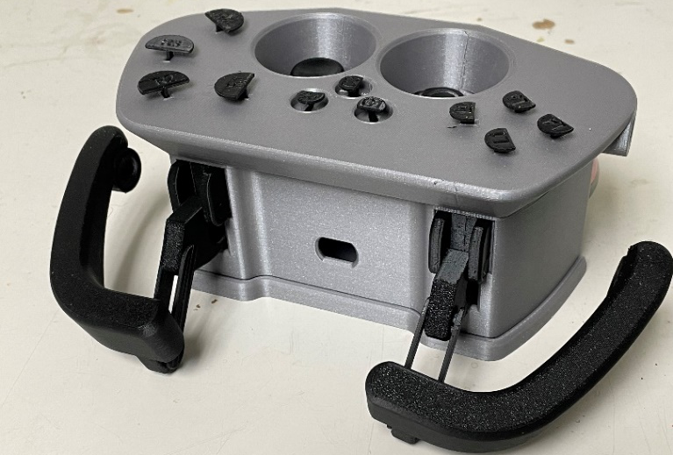
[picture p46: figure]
The second step for installed the triggers.

## Step 6: Mounting the Trigger to the Top Face

Attach the “Trigger Arms” to the sides of the “Face” by feeding the “Trigger Shaft” through the arms and into the side hole of the Face. The Trigger Shaft must seat in all the way and tape can be used use to properly secure it as shown below. This part should be kept removable, so do not use glue.

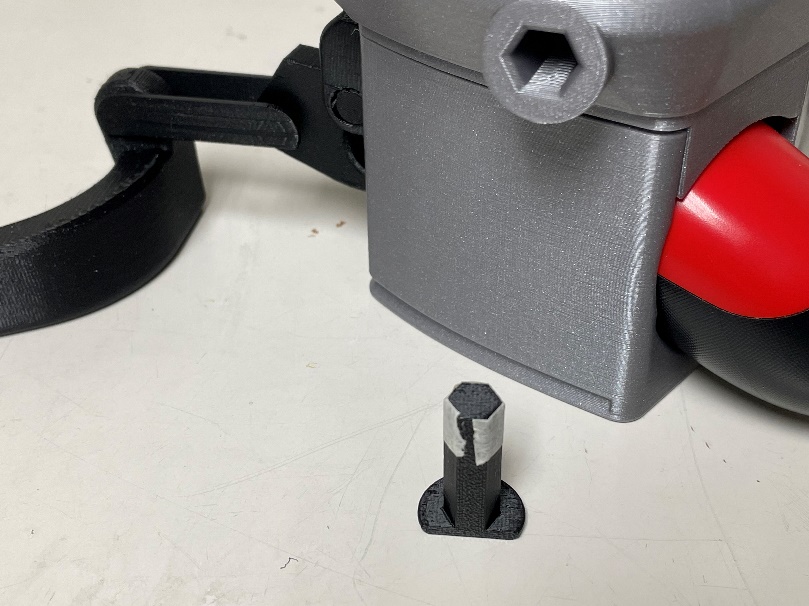
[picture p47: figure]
The third step for installed the triggers.
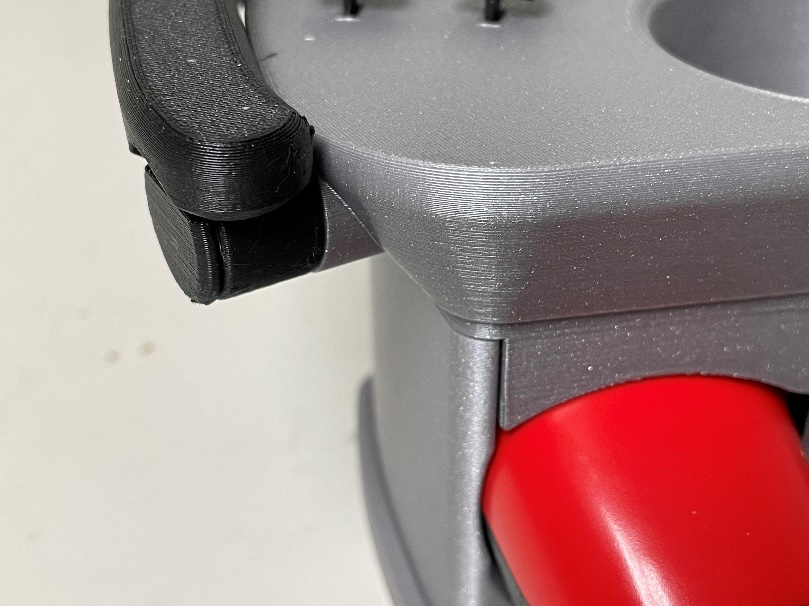
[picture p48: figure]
The final step for installing the triggers.

## Assembly Finished

The device is now fully assembled. Follow user guide for steps to install the controller and joysticks.

© 2023 by Neil Squire / Makers Making Change This work is licensed under the CC BY SA 4.0 License: http://creativecommons.org/licenses/by-sa/4.0 Files available at https://makersmakingchange.com/project/adaptive-case-for-ps4-controller Page 1 of 4

V1.0 | February 2023 Adaptive Case for PS4 Controller Assembly Guide

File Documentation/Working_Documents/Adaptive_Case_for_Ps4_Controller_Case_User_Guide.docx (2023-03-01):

## Introduction

The Adaptive Case for PS4 Controller is an inexpensive and non-destructive controller modification designed to make the stock PS4 controller more accessible. This device aims to assist those with limited hand dexterity by enlarging and spreading out the buttons on the PS4 controller. This device can be mounted to a surface so that both hands can freely operate the controls.

## Features

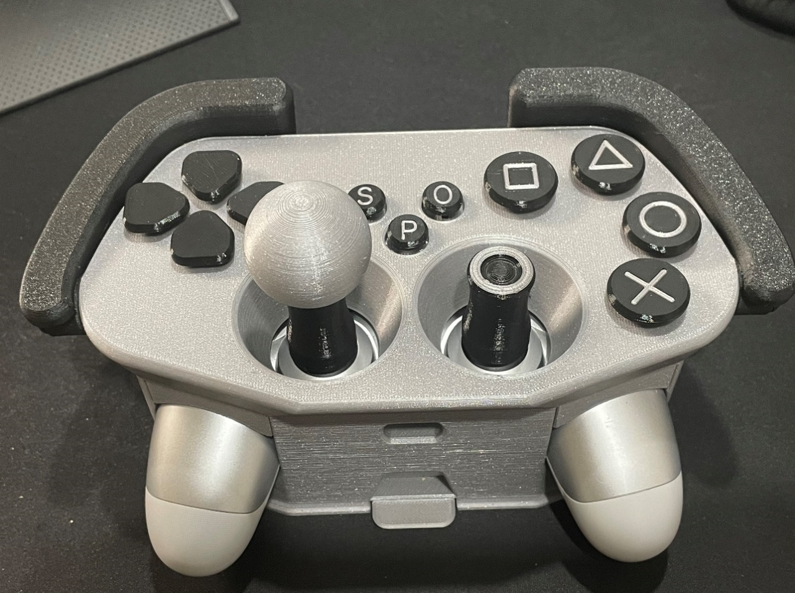
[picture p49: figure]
A PS4 controller in a grey and black 3D printed adaptive case.

## Compatibility

Note that the PS4 controller can be used for PC based gaming.

Platforms: PlayStation 4, PC

Controllers: DualShock 4 Controller

## Specifications

Weight (Case only) | Length | Width | Height
~200g | ~22 cm | ~12 cm | ~8 cm

## Usage

To use this device, the DualShock 4 controller must be mounted into the case and the preferred joysticks installed onto the controller.

### Installing the Controller

To install the PS4 controller into the adaptive case, lift the top of the case and swivel it behind as shown below. Place the controller into the case and resecure the top by aligning the lip of the case with the slots in the top face. Press firmly to snap these two halves together.

Note: Joysticks can only be installed once the controller has been mounted.

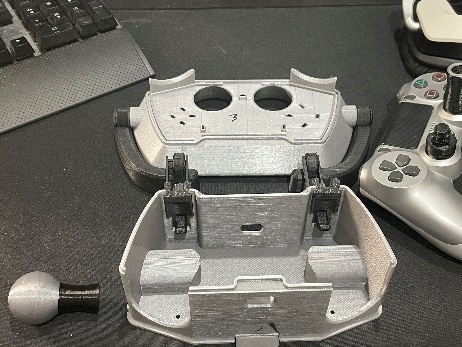
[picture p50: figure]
A grey and black 3D printed adaptive case with the top removed and swiveled behind.
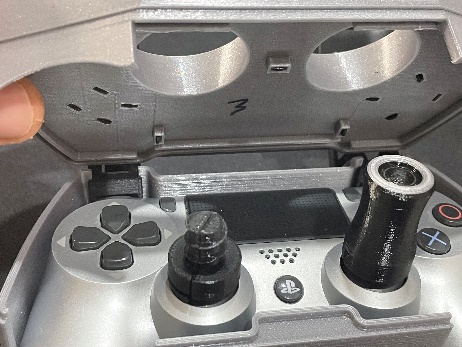
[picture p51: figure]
The inside of a half opened adaptive case showing a PS4 controller inside.
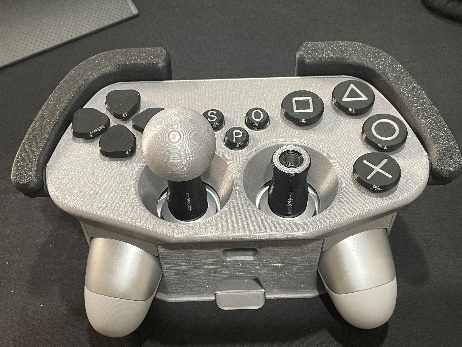
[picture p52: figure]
A PS4 controller inside a grey and black 3D printed adaptive case

To remove the controller from the case, follow the installation instructions in reverse order, starting by removing the large joysticks as they will not fit through the top face.

### Installing the Joysticks

There are a few different adaptive joystick options that are shown in the next section. Place each half of the 3D-printed screws around the joysticks on the controller. Press the halves together to form a solid screw and thread on your preferred joystick topper.

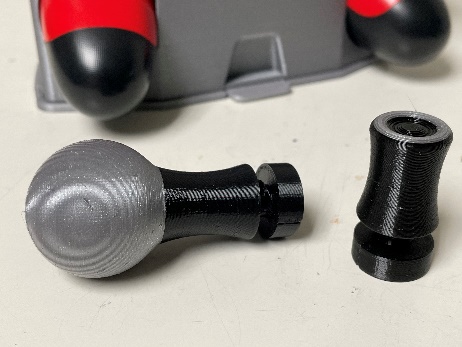
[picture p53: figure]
A close up of a grey and black ball shaped joystick and a black cylindrical joystick.
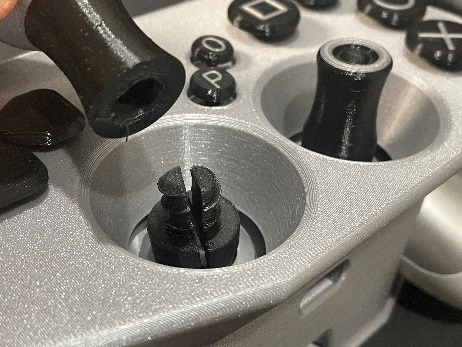
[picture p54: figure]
A close up a 3D printed joystick being screwed onto a PS4 controller that's mounted inside an adaptive case.
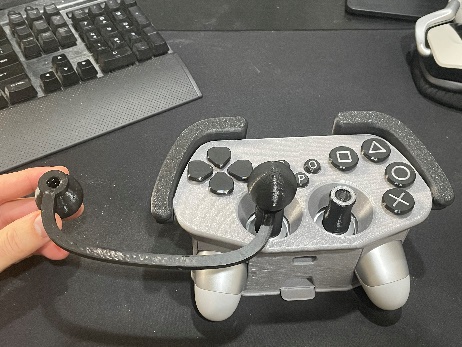
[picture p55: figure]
A grey and black 3D printed adaptive case with a helper joystick attached.

### Joystick Topper Options

Topper Design | Usage

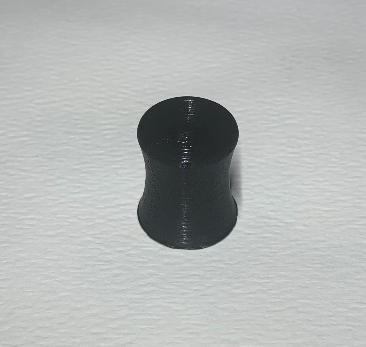
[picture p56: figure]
A black 3D printed joystick topper with a concave top.

Extended Joystick | A standard extended joystick topper with a concave top face for grip. To allow room for both joysticks to move, it is recommended to use this topper along side one of the others.

Ball Joystick

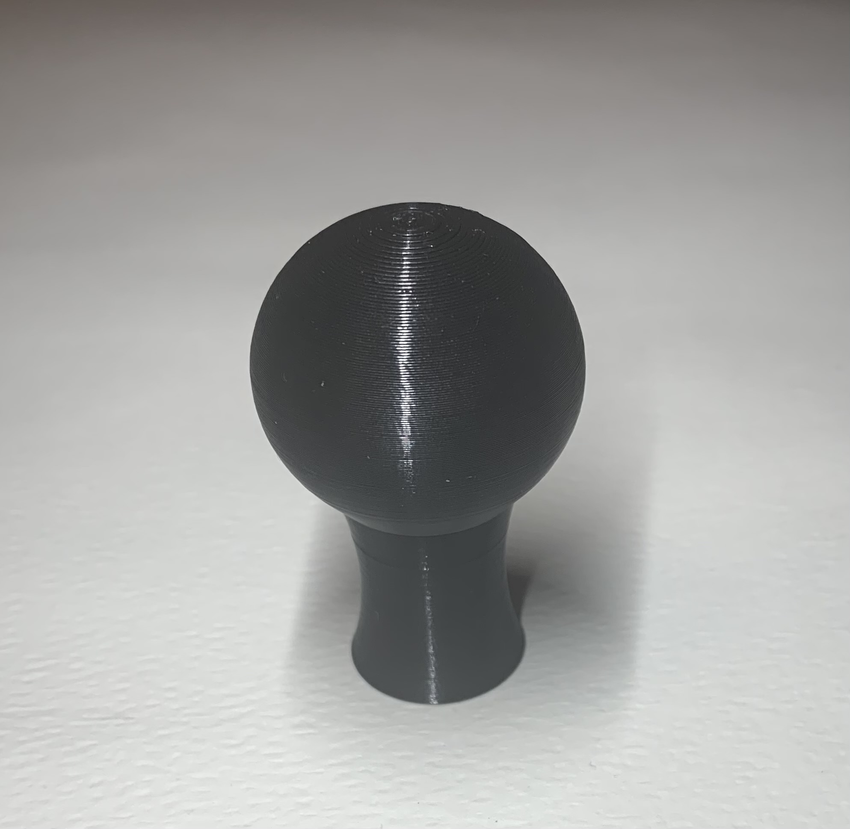
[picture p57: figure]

The ball joystick topper gives lots of room to grip the controller’s joystick. Its length allows the joystick to be operated with very little force.

Ring Joystick

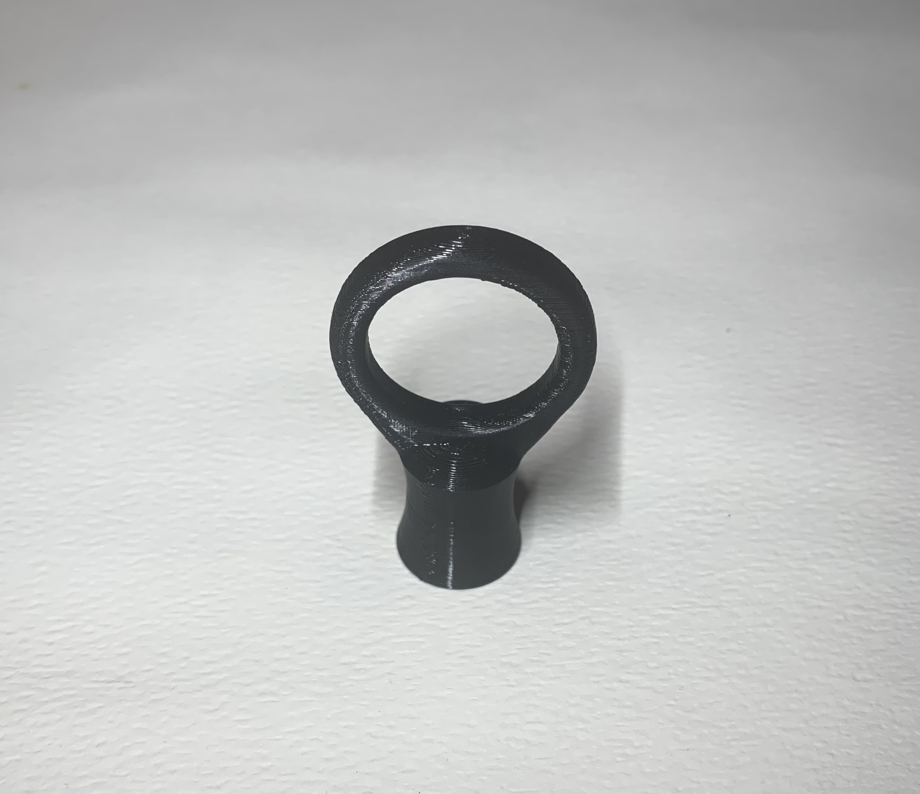
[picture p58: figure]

The Ring Joystick allows you to insert a thumb finger into the topper to aid in controlling the joystick.

Double Joystick

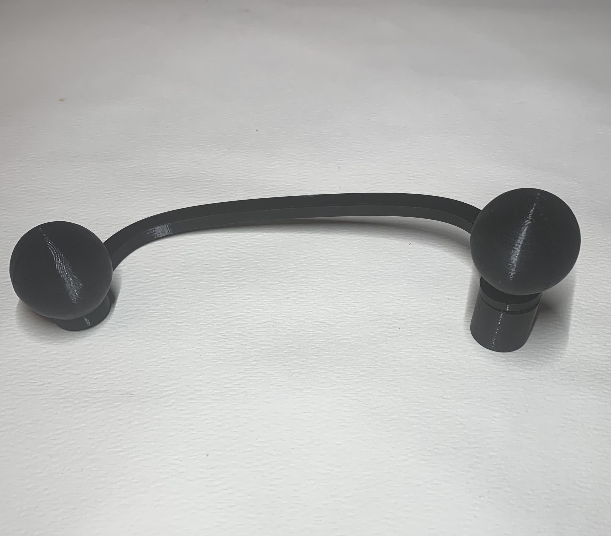
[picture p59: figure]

The Double Joystick adds a second Joystick topper that can be operated by secondary user. This allows the secondary user to help assist with the controls.

### Mounting the Device

This device comes with an optional dock that allows you to secure the adaptive case to a table or surface. This may benefit users who find it challenging to hold onto the device. The low profile “Dock” can be screwed to a surface before sliding in the case to click-lock it in place. The front tab can be pushed down to unlock and remove the case from the dock.

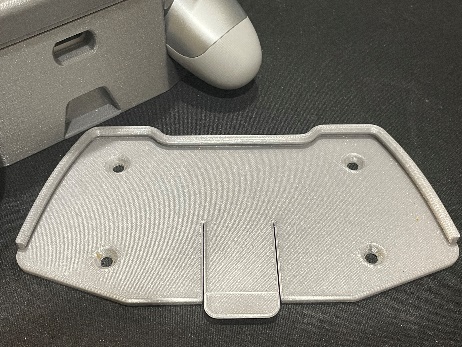
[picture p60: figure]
A grey low profile 3D printed dock with four holes to allow it to be screwed to a surface.
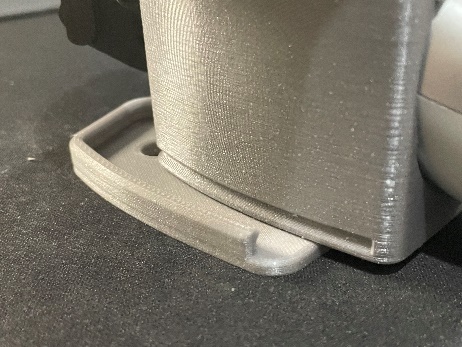
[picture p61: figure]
A close up of an adaptive case being slid into a dock.
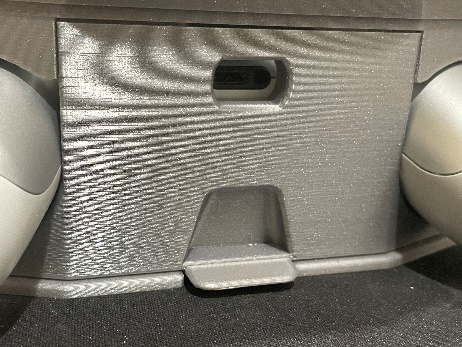
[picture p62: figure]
A close up of an adaptive case being secured into a dock with a front tab.

## Cleaning

The device can be cleaned by disassembling and removing the controller before wiping down the pieces with a damp cloth or plastic safe cleaning wipes.

© 2023 by Neil Squire / Makers Making Change This work is licensed under the CC BY SA 4.0 License: http://creativecommons.org/licenses/by-sa/4.0 Files available at https://makersmakingchange.com/project/adaptive-case-for-ps4-controller Page 1 of 4

V1.0 | February 2023 Adaptive Case for PS4 Controller user Quick Guide

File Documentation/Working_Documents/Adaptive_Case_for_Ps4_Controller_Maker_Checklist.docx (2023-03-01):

# Maker To Do List

- Read through the Assembly Guide to become familiar with required components, tools, supplies, safety gear, and overall assembly steps.
- Talk to User about customization options (e.g., color, any special requests, etc.)
- Gather tools, supplies, and safety equipment.
- Assemble the device.
- Test the device.
- Print “User Quick Guide”.

# Items to Give to User

- Assembled, tested device.
- “User Quick Guide”

© 2023 by Neil Squire / Makers Making Change This work is licensed under the CC BY SA 4.0 License: http://creativecommons.org/licenses/by-sa/4.0 Files available at https://makersmakingchange.com/project/adaptive-case-for-ps4-controller Page 1 of 4

V1.0 | February 2023 Adaptive Case for PS4 Controller Maker Checklist

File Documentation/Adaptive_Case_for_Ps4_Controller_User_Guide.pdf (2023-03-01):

V1.0 | February 2023

## Adaptive Case for PS4 Controller

## USER QUICK GUIDE

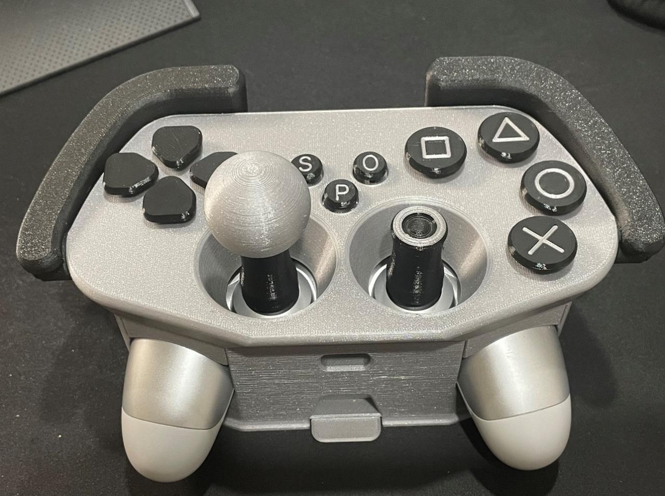
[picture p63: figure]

© 2023 by Neil Squire / Makers Making Change (https://www.neilsquire.ca/) This work is licensed under the CC BY SA 4.0 License: http://creativecommons.org/licenses/by-sa/4.0 Files available at https://makersmakingchange.com/project/adaptive-case-for-ps4-controller

### Introduction

The Adaptive Case for PS4 Controller is an inexpensive and non-destructive controller modification designed to make the stock PS4 controller more accessible. This device aims to assist those with limited hand dexterity by enlarging and spreading out the buttons on the PS4 controller. This device can be mounted to a surface so that both hands can freely operate the controls.

### Features

### Compatibility

Note that the PS4 controller can be used for PC based gaming.

Platforms: PlayStation 4, PC

Controllers: DualShock 4 Controller

### Specifications

Weight (Case only) | Length | Width | Height
~200g | ~22 cm | ~12 cm | ~8 cm

## USER QUICK GUIDE


© 2023 by Neil Squire / Makers Making Change (https://www.neilsquire.ca/)

### Usage

To use this device, the DualShock 4 controller must be mounted into the case and the preferred joysticks installed onto the controller.

Installing the Controller
To install the PS4 controller into the adaptive case, lift the top of the case and swivel it behind as shown below. Place the controller into the case and resecure the top by aligning the lip of the case with the slots in the top face. Press firmly to snap these two halves together.

Note: Joysticks can only be installed once the controller has been mounted.

To remove the controller from the case, follow the installation instructions in reverse order, starting by removing the large joysticks as they will not fit through the top face.

Installing the Joysticks
There are a few different adaptive joystick options that are shown in the next section. Place each half of the 3D-printed screws around the joysticks on the controller. Press the halves together to form a solid screw and thread on your preferred joystick topper.

## USER QUICK GUIDE


© 2023 by Neil Squire / Makers Making Change (https://www.neilsquire.ca/)

Joystick Topper Options
Topper Design | Usage
Extended Joystick | A standard extended joystick topper with a concave top face for grip. To allow room for both joysticks to move, it is recommended to use this topper along side one of the others.
Ball Joystick | The ball joystick topper gives lots of room to grip the controller’s joystick. Its length allows the joystick to be operated with very little force.
Ring Joystick | The Ring Joystick allows you to insert a thumb finger into the topper to aid in controlling the joystick.
Double Joystick | The Double Joystick adds a second Joystick topper that can be operated by secondary user. This allows the secondary user to help assist with the controls.

## USER QUICK GUIDE


© 2023 by Neil Squire / Makers Making Change (https://www.neilsquire.ca/)

Mounting the Device
This device comes with an optional dock that allows you to secure the adaptive case to a table or surface. This may benefit users who find it challenging to hold onto the device. The low profile “Dock” can be screwed to a surface before sliding in the case to click-lock it in place. The front tab can be pushed down to unlock and remove the case from the dock.

### Cleaning

The device can be cleaned by disassembling and removing the controller before wiping down the pieces with a damp cloth or plastic safe cleaning wipes.

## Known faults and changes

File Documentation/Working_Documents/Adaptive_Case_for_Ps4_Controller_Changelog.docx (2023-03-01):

# Version 1.0 | 2023/January/24

- Design by Cisco (https://www.printables.com/social/28161-cisco/models) posted on Printables (https://www.printables.com/model/91884-ps4-case-adapter)
- Licenced under GNU GENERAL PUBLIC LICENSE (https://www.gnu.org/licenses/old-licenses/gpl-2.0.html)
- A non-destructive PS4 controller adaption with larger buttons spread apart.

© 2023 by Neil Squire / Makers Making Change This work is licensed under the CC BY SA 4.0 License: http://creativecommons.org/licenses/by-sa/4.0 Files available at https://makersmakingchange.com/project/adaptive-case-for-ps4-controller Page 1 of 4

V1.0 | February 2023 Adaptive Case for PS4 Controller changelog

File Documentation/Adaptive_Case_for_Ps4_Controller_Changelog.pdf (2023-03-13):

V1.0 | February 2023

## Adaptive Case for PS4 Controller

## CHANGELOG

© 2023 by Neil Squire / Makers Making Change (https://www.neilsquire.ca/) This work is licensed under the CC BY SA 4.0 License: http://creativecommons.org/licenses/by-sa/4.0 Files available at https://makersmakingchange.com/project/adaptive-case-for-ps4-controller

## Version 1.0 | 2023/January/24

- Design by Cisco (https://www.printables.com/social/28161-cisco/models) posted on Printables (https://www.printables.com/model/91884-ps4-case-adapter)
- Licenced under GNU GENERAL PUBLIC LICENSE (https://www.gnu.org/licenses/old-licenses/gpl-2.0.html)
- Alteration by Makers Making Change
- Added clearance to joystick screws.
- Changes print orientations of joystick screws for increased strength.
- A non-destructive PS4 controller adaption with larger buttons spread apart.
